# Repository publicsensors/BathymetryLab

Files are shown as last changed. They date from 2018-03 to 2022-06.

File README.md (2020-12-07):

# [Sound and the seafloor: Determining bathymetry using student-built acoustic sensors](https://doi.org/10.5670/oceanog.2020.305)

### Robert Levine<sup>1</sup>, Sasha Seroy<sup>1</sup>, and  Daniel Grünbaum<sup>1</sup>
<sup>1</sup> School of Oceanography, University of Washington, Seattle, WA, USA.

The article this repository supports was published in the September 2020 volume of <a href="https://doi.org/10.5670/oceanog.2020.305" target="_blank">*Oceanography*</a>.

This repository serves as a central location for the ultrasonic distance sensor Bathymetry Lab module and related activities for outreach, K-12, and undergraduate teaching. There are two sections to this repository, [**BathymetryLab**](https://github.com/publicsensors/BathymetryLab/tree/master/BathymetryLab) which contains the materials necessary to complete the seafloor activity, and [**AddOnsAndExtensions**](https://github.com/publicsensors/BathymetryLab/tree/master/AddOnsAndExtensions) which contains additional lab activities and code that can be used with the ultrasonic distance module.

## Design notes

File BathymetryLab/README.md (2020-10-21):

# BathymetryLab
## **MaterialsForInstructors**
### BathymetryLab_Instructor.ipynb
IPython notebook containing instructions and example figures for the bathymetry lab activity.
___
## **Handouts**
### BathymetryLab.ipynb
IPython notebooks for use to measure and map the change in seafloor using a JSN-SR04T waterproof transducer.  Students collect data at fixed intervals along a dock or pier and then create a plot of the bathymetry using python on their own computers. `BathymetryLab.ipynb` is the empty activity notebook.

### BathymetryLab_Pyserial.ipynb
Identical lab activity to `BathymetryLab.ipynb` however the notebook utilizes `pyserial` to record measurements directly from a USB-connected ESP8266 rather than requiring students to input readings by hand.
___
## **Microcontroller**
This folder contains the basic libraries and codes for using the HC-SR04 or JSN-SR04T acoustic sensor via MicroPython, though alternative microcontroller systems can be used to conduct the activity. Examples and code in this repository are for use with an ESP8266 processor microcontroller such as the [Feather HUZZAH with ESP8266](https://www.adafruit.com/product/2821).

Another example of sensor assembly using a [Feather STM32F405 Express](https://www.adafruit.com/product/4382) and [PyBoard](https://store.micropython.org/) microcontrollers can be found in the [Microcontroller Kits repository](https://github.com/publicsensors/MicrocontrollerKits/tree/master/Sensors/Acoustic) within the PublicSensors organization.

####  hcsr04.py
The driver for measuring distance using the HCSR04 sensor.  Required parameters are GPIO `trigger_pin` and `echo_pin`, with optional arguments for sound speed, `c`, and timeout. Private functions to intialize the sensor parameters and send signal.  `distance` function returns distance in millimeters.
```python
import hcsr04
sensor = hcsr04.HCSR04(trigger_pin=12, echo_pin=14, c=343) # define pins and speed of sound
sensor.distance() # returns distance in mm
```

#### firmware-combined.bin
Micropython firmware for ESP8266 boards. See [Getting started with MicroPython on the ESP8266](https://docs.micropython.org/en/latest/esp8266/tutorial/intro.html) for details on deploying the firmware.

#### boot.py
Basic boot initialization file example.

#### print_distance.py
Using the `hcsr04.py` driver to continuously measure and print distance at set interval.
```python
import print_distance
print_distance.print_distance(trigger_pin = 12, echo_pin = 14, c=343, interval=1) #interval is time in seconds
```
### SensorPartsList.xlsx
Excel spreadsheet with details and approximate pricing for sensor components needed to conduct the activity. Additional recommendations and instructions on assembly specific to this activity are found in the **MaterialsForInstructors** folder.

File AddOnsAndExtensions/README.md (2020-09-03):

# AddOnsAndExtensions

## **SpeedOfSound**
### SpeedOfSound_Instructor.ipynb
IPython notebook containing instructions and example figures for a lab activity to approximate the speed of sound in air using measurements collected at a fixed distance over variable values of `c`, sound speed.  Requires micropython firmware on ESP8266 or PyBoard microcontrollers and HC-SR04 sensor. `SpeedOfSound.ipynb` is the empty activity notebook.

### SpeedOfSound.ipynb
Contains all of the instructions for students to complete the assignment described above, but leaves out example executable code and data for figures.

### SpeedOfSound_Pyserial.ipynb
Identical lab activity to `SpeedOfSound.ipynb` however the notebook utilizes `pyserial` to record measurements directly from a USB-connected ESP8266 rather than requiring students to input readings by hand.

---

## **WaveTankLab**
Code for conducting an extension activity using multiple distance sensors to measure wave height at different positions in a wave tank. Students explore signal processing and implications of variable sampling frequencies.

### HCSR04_Timer.py
Runs HCSR04 to collect distance measurements at a fixed time interval using a periodic timer, with option to write to file.

###  HCSR04_TrigRx.py
Runs HCSR04 to collect distance measurements at a fixed time interval using a periodic timer, with option to write to file.  The timer is initiated from an external interrupt.

###  xcorrTimeSeries.py
Reads .txt files produced by HCSR04_Timer.py or HCSR04_SampleCt.py to create time series scatter plots of distance measurements.  User must define directory of file locations.

---

## **AdditionalCode**
Extra materials for reading and plotting recorded files.

### plot_recorded_distance.py
Reads and plots time series of distance data recorded in text file using `HCSR04_Timer.py` in the **WaveTankLab** or `record_distance.py`.

### record_distance.py
Using the hcsr04 driver to continuously measure distance at set interval and record to a text file. The output file can be read by the `plot_recorded_distance.py` script. Calling, as commented in the file, is completed as:
```Python
import record_distance
prefix = 'NAME'
interval_ms = 1 # sampling interval in milliseconds, 100 is 10Hz
record_time = 10 # time to record in seconds
trigger_pin_num = 12 # trigger pin connection to HCSR04 sensor
echo_pin_num = 14 # echo pin connection to HCSR04 sensor
sound_speed = 343 # Sound speed in m/s
write_file = 1

record_distance.record_dist(prefix,interval_ms,record_time, trigger_pin_num, echo_pin_num, sound_speed, write_file)
```

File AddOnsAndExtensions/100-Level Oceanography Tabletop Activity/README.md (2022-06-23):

# UW Oceanography Introduction to Environmental Monitoring and Technology (OCEAN 161)
This repository contains materials required to conduct the bathymetry lab acoustic sensor table top acitvity and lesson plan. This was conducted in a 100-level introductory oceanography course which focused on exploring tools and techniques scientists use to monitor the ocean and environment. This course is geared towards students with no prior oceanography or technology knowledge and enrolls many non-science majors. 

### Lab activity
`StudentWorksheet.docx` is the student activity sheet that walks through the lab procedure to build, calibrate, and simulate use to map bathymetry at two different spatial resolutions. The lab acitivity requires the `GraphingTemplate.xlsx` where students input their collected data and the template graphs it automatically to better facilitate data interpreatation and discussion. 

### Lab Preparation
To prepare for the lab, instructors must acquire the necessary parts and construct bathymetry boxes. In this iteration bathymetry boxes were constucted using black foam board and a seafloor feature was created within the box also using foam board. The boxes are 14" long x 10" tall x 4" wide and the faces are attached using hot glue. See photos below for top and side views of bathymetry boxes. 

topView    sideView

Electronic components needed include a Pyboard (or other microcontroller running MicroPython), jumper wires, and an hcsr-04 acoustic sensor. The microcontroller needs to be loaded with `hcsr04.py` and `distance_sensor.py`. Provided here are a file to 3D print a holder for the sensor, `SensorHolder.stl`,  to be able to slide it over the bathymetry box and create the table top bathymetry boxes required for the lab. Other materials needed include a ruler to calibrate the sensor, and an index card.

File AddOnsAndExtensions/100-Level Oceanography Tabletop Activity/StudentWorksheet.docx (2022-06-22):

Overview: In today’s lab, you will be building, calibrating, and using simple acoustic sensors to explore how sound is used in seafloor mapping applications. Work in lab groups of 3-4 students to complete this assignment.

Part 1: Build a simple acoustic sensor

The acoustic sensor you will use in this lab (HCSR-04) transmits sound and measures time elapsed until receiving it back. Using the speed of sound in the medium (e.g. in air, freshwater, or seawater) the sensor can calculate how far away an object or surface is just by measuring the time between sending out a sound, and receiving the echo. In this lab, we will just use the speed of sound in air (343 m/s).

Materials needed: acoustic sensor, four jumper wires, Pyboard microcontroller, USB cable, laptop

1. Connect the acoustic sensor to the microcontroller using jumper wires as shown below:

VCC (distance sensor) → V+ (Pyboard) | GND (distance sensor) → GND (Pyboard)
TRIG (distance sensor) → X10 (Pyboard) | ECHO (distance sensor) → X9 (Pyboard)

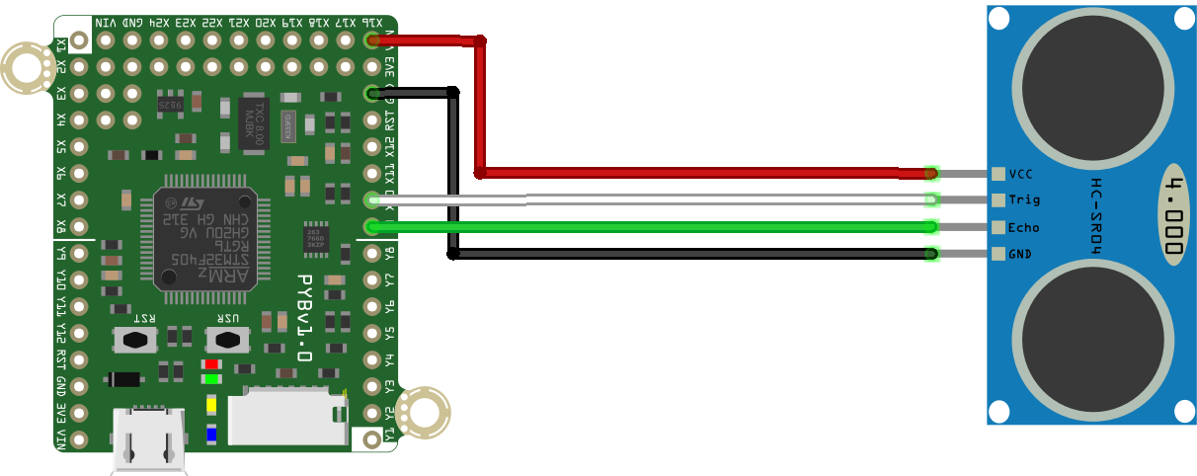
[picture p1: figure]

2. Connect the Pyboard to a laptop using the microUSB-USB cable. It should come up as a flashdrive. When you are ready to unplug your Pyboard after the lab, eject it properly just as you would a flashdrive.
3. In Google Chrome, launch the Beagle Term app and connect to your sensor. You can find this by searching the Chrome store or by searching “Beagle Term” in Google. This app lets you directly communicate with a microcontroller like the Pyboard you just attached the acoustic sensor to.

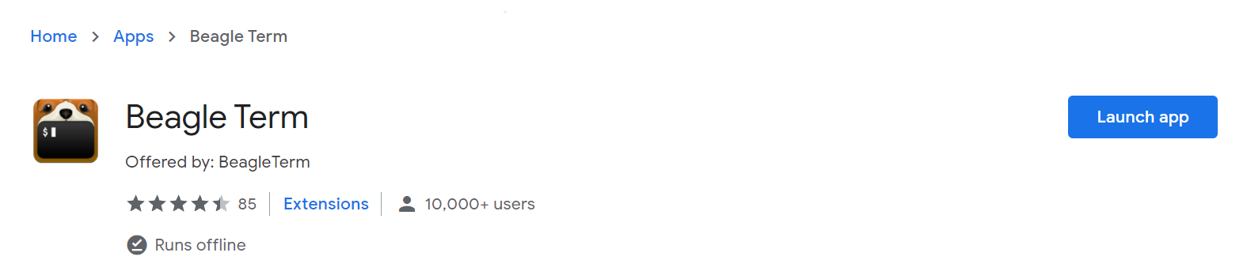
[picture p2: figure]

4. Beagle Term should automatically detect the settings you need. Click ‘Connect’ and make sure to click inside the window and press Enter. Note: If using a Mac, the Port may not automatically detect and you may need to try a few different ports in the drop down menu until you find the correct one that enables you to connect.

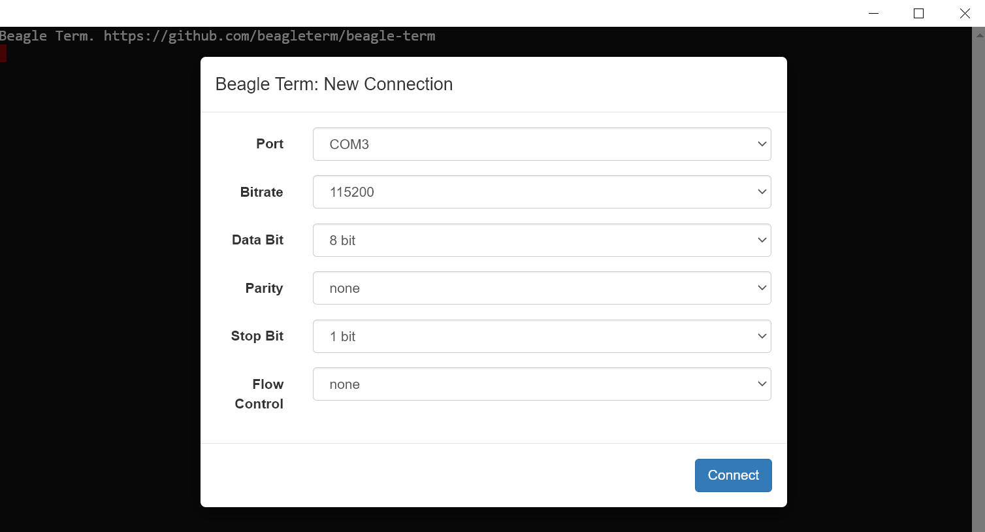
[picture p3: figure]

5. When you connect, the screen should look like the image below. The rectangular cursor after >>> indicates you are ready to type code. If you do not get this welcome screen use Ctrl+D to refresh the session.
6. In Beagle Term, type the following command and hit Enter to load the necessary function which will enable you to collect distance measurements. This command loads the function read_distance from the distance_sensor library on the Pyboard.
7. To get a distance measurement (in mm), use the read_distance function you just loaded by typing read_distance() and then hit Enter. A distance reading should print on the line below. To take another measurement, hit the up arrow to repeat the previous command without retyping it.

Test out your sensor by moving your hand closer to the sensor and then take a reading. Then move your hand and farther away and take another reading. Observe how the distance detected from your hand to the sensor changes.

Part 2: Calibrate the acoustic sensor (40pts)

Materials needed: Constructed acoustic sensor, ruler, index card

You will now assess the accuracy of the acoustic sensor you just built. This is known as calibration. To calibrate an instrument, you compare against a known standard. Since your sensor measures distance acoustically, you can compare it to a ruler (a known standard of distance).

1. Place a ruler on the table with the distance sensor set at zero 0 mm.
2. Place an index card 5cm (50mm) away from the sensor and take 5 replicate readings. Record readings in the table below and calculate the mean distance based on your 5 readings. Repeat the process for each of the distances listed below. (12pts)

Ruler distance (mm) | Sensor Distance 1 (mm) | Sensor Distance 2 (mm) | Sensor Distance 3 (mm) | Sensor Distance 4 (mm) | Sensor Distance 5 (mm) | Mean Distance (mm)
50
100
150
200
250
300

3. Assess the precision of your acoustic sensor using your distance data from 200mm. Recall that calculating the standard deviation of your measurements will give you a measure of precision. Show your work. (4pts)

Standard deviation (σ) = measure of the spread of a set of data points | σ= √((Σ(x_i - μ)^2)/n)

n = number of values in set x_i = each value from the set

4. What does this mean about how repeatable or precise your distance measurements are? (2pts)
5. Create a calibration curve for your acoustic sensor. This will help you assess the accuracy of your sensor. Accuracy is a measure of how close your sensor readings are to the true value (ruler measurement). To create the calibration curve, make a graph of the ruler distance vs. the mean measured distance using the six points from your table above. Use the Excel template (Tab 1) to help you. Open the spreadsheet locally in Excel, not in Google Sheets to preserve the functionality. Attach the Excel file with completed graph to your assignment submission. (12pts)
6. Report the equation of the trendline for your calibration. What does the slope mean about the calibration? What does the intercept mean about the calibration? (5pts)
7. Using your answers above, how accurate do you think your acoustic sensor is? (3pts)
8. Are there any differences in your sensor’s accuracy when reading short vs. long distances? How do you know? (2pts)

Part 3: Use the acoustic sensor to map the seafloor (48pts)

In this part you will use your sensor to measure the height of the seafloor along a transect using a Bathymetry Box. Inside the Bathymetry Box is a replica of a seafloor feature you will try to map using your acoustic sensor. This is analogous to how oceanographers map seafloor features from a ship on the surface.

1. Get a Bathymetry Box and identify the measuring tape along the top of it. This will help you plan out where to take distance measurements.
2. Insert the acoustic sensor facing downward into the frame which will slide along the top of the box.
3. Take distance measurements every three inches and record them in a table. Like you did in Part 2, take 5 replicate readings at each sampling position, and calculate the mean. (8pts)

Length along transect (inches) | Sensor Distance 1 (mm) | Sensor Distance 2 (mm) | Sensor Distance 3 (mm) | Sensor Distance 4 (mm) | Sensor Distance 5 (mm) | Mean Distance (mm)
1”
4”
7”
10”
13”

4. Now increase the spatial resolution of your measurements. Take distance measurements as you did above every inch and record them in the table below. (16pts)

Length along transect (inches) | Sensor Distance 1 (mm) | Sensor Distance 2 (mm) | Sensor Distance 3 (mm) | Sensor Distance 4 (mm) | Sensor Distance 5 (mm) | Mean Distance (mm)
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
When you are ready to unplug your Pyboard after the lab, eject it properly just as you would a flashdrive. Do not just unplug it!!!

5. Create a graph which combines the data from the above two tables. Plot length along transect vs. the mean depth calculated using your acoustic sensor. Use the Excel Template (Tab 2) to help you. Open the spreadsheet locally in Excel, not in Google Sheets to preserve the functionality. Attach the Excel file with completed graph to your assignment submission. (12pts)
6. How did increasing the resolution of your measurements affect your ability to characterize the bathymetry? Provide an example from your graph. (5pts)
7. What feature(s) could you identify from your acoustics measurements? (3pts)
8. What would be the ideal spatial resolution to sample the transect you sampled? Why? (2pts)

Reflection questions (12pts)

a. What are the overall benefits of using these acoustic tools? (3pts)
b. What are the overall limitations of using these acoustic tools? (3pts)
c. Over what time and space scales could these acoustic tools be helpful to observing the environment? (4pts)

Feedback: What did you think of this lab? What did you learn from it? Did you enjoy it? What can be improved? (2 pts)

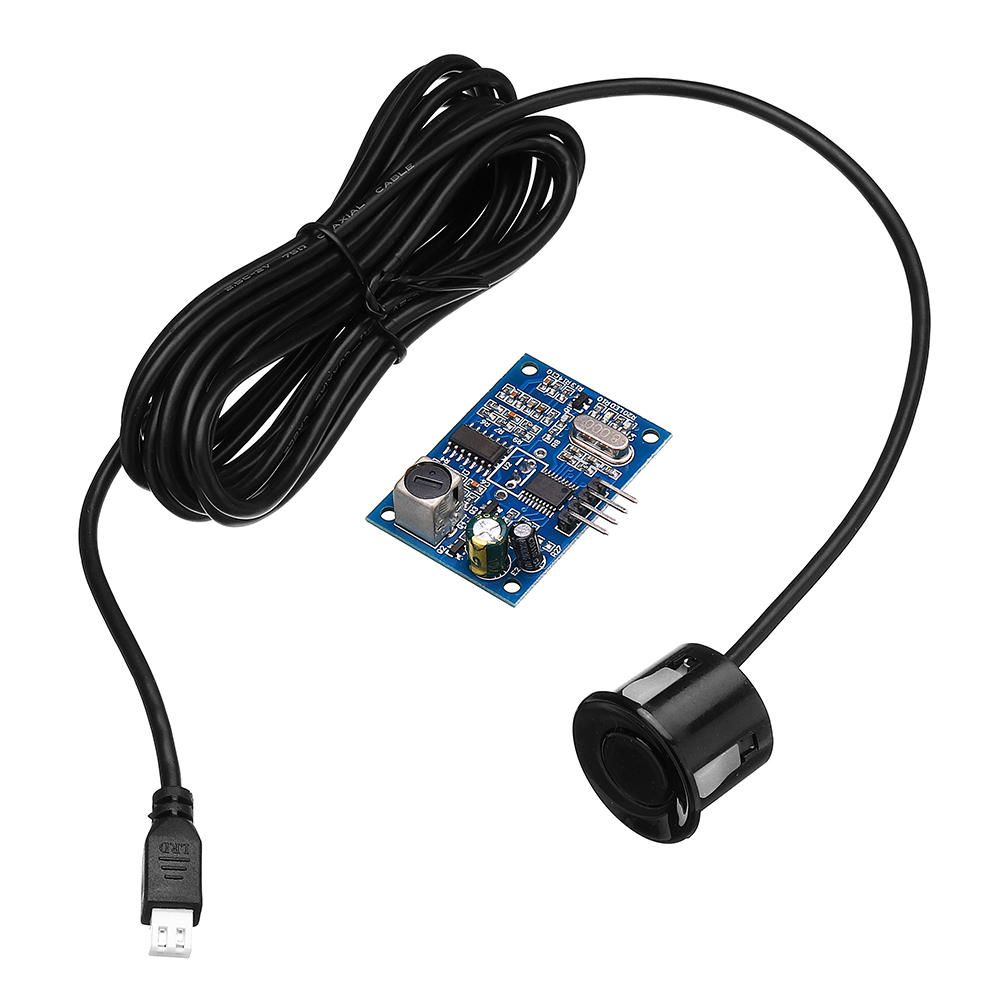
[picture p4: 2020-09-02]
images/jsnsr04.png

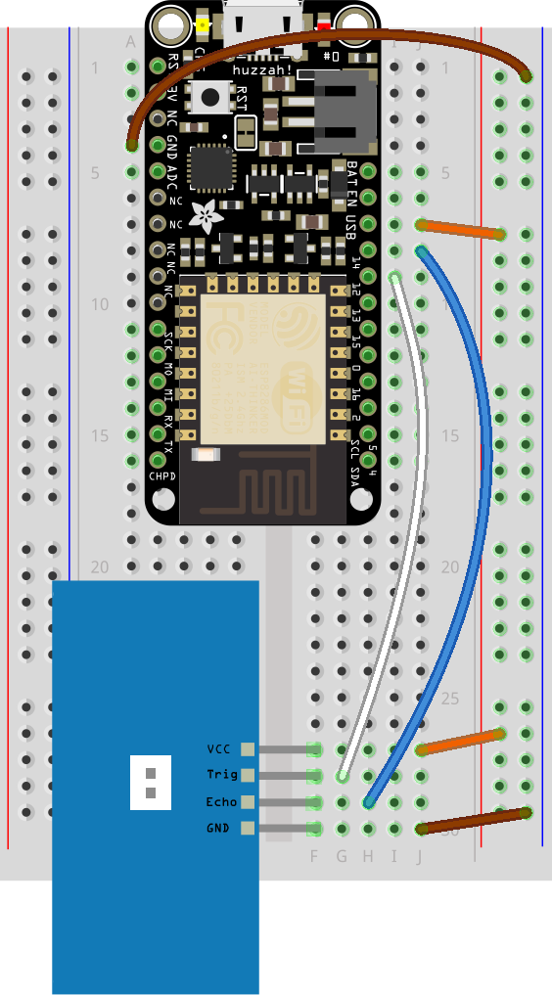
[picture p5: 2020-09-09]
images/Feather_jsnsr04.png

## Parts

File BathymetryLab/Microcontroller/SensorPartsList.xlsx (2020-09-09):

For a class of 20 students
Total 12 kits (10 groups of 2 students + 2 extra kits just in case)
Sensor components | Cost ($) | Number | Total ($) | Notes | Link for example materials
Feather HUZZAH with ESP8266 | 16.95 | 12 | 203.4 | *See Below | https://www.adafruit.com/product/2821
M-M jumpers (pack of 20) | 1.95 | 4 | 7.8 | **See Below | https://www.adafruit.com/product/1956
JSN-SR04T Waterproof Ultrasonic Module | 10.95 | 12 | 131.4 |  | https://www.jameco.com/z/JSN-SR04T-Arndt-Waterproof-Ultrasonic-Module-JSN-SR04T-Integrated-Distance-Measuring-Transducer-Sensor-for-Arduino_2279255.html
microUSB cable | 2.95 | 12 | 35.4 |  | https://www.adafruit.com/product/592
Half-size bradboard | 5 | 12 | 60 | **See Below | https://www.adafruit.com/product/64
Total ($) |  |  | 438
Additional
*Boards ship with header pins which will need to be soldered for use with either a breadboard or F-F jumpers for connection to the distance module.
**In place of a breadboard, students can use F-F jumpers to directly connect the JSN-SR04T module to the header pins of the microcontroller (https://www.adafruit.com/product/1950).

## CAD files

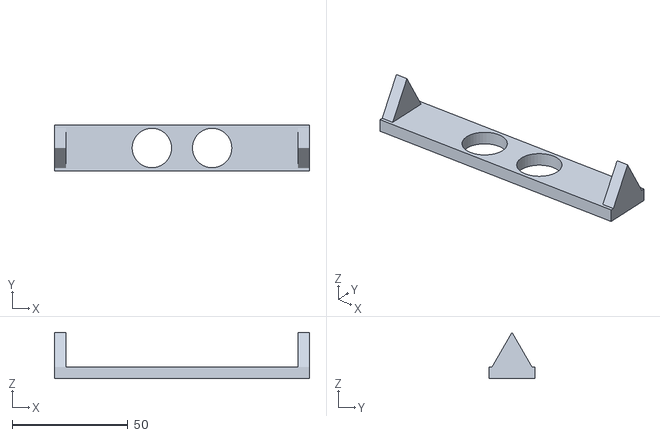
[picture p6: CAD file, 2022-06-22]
AddOnsAndExtensions/100-Level Oceanography Tabletop Activity/SensorHolder.stl
110.0 x 20.0 x 20.0

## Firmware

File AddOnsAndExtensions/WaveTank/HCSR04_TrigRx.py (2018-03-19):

#
#  Collect data from an HCSR04 ultrasonic sensor by setting a timer to sample at
# a fixed interval for a given length of recording
   # Free up heap space

"""
# Before calling HCSR04_TrigRx, the rtc on the ESP8266 must be synced with NTP:

from network import WLAN, STA_IF
wlan = WLAN(STA_IF)
wlan.active(True)
wlan.connect('OTCnet','ocN3five1_OTc')
import ntptimeTS3231
ntptimeTS3231.settime()

# Once the onboard clock is set, we have to define all of the parameters for running
#  An example of a typical execution sequence:
#---------------------------------------
# Sampling parameters - must be defined
#---------------------------------------
 	
import HCSR04_TrigRx

prefix = 'Position2_SlowWave'
interval_ms = 100 # sampling interval in milliseconds, 100 is 10Hz
record_time = 60 # time to record in seconds
trigger_pin_num = 12 # trigger pin connection to HCSR04 sensor
echo_pin_num = 13 # echo pin connection to HCSR04 sensor
sound_speed = 343 # Sound speed in air in m/s
write_file = 1 # 0 to just print values, 1 to save to text file with file prefix defined above

HCSR04_TrigRx.measure_dist(prefix,interval_ms,record_time,
trigger_pin_num, echo_pin_num, sound_speed, write_file)

"""

#
from machine import RTC, Pin, Timer, unique_id
import utime
from ubinascii import hexlify
from gc import collect
from hcsr04 import HCSR04
from os import rename, listdir
collect()

def measure_dist(prefix='ocn351',interval_ms=100, record_time = 5,trigger_pin_num = 12, echo_pin_num=13, sound_speed=343, write_file = 0):
	global startSampleFlag
	startSampleFlag = 0
	sensor = HCSR04(trigger_pin = trigger_pin_num, echo_pin = echo_pin_num, c=sound_speed) # Set up the HCSR04
        print('\nUsing sampling interval ',interval_ms,' milliseconds...')
	print('Recording data for ',record_time,' seconds...\n')
	print('\n\n****Beginning Recording ****\n\n')
	runTimer = Timer(-1) # Initiate a timer
	tmp_file='tmp.txt'  # A temporary filename; we will write partial data to this file, and rename only if sampling
	rtc = RTC() # intiate a real-time clock variable
	ID=hexlify(unique_id()).decode('utf-8') # Unique ID of the microprocessor
	timestamp=str(utime.mktime(rtc.datetime())) # Create a string time stamp from the real-time clock
	filename=prefix+'_'+ID+'_'+timestamp+'.txt' # Define a filename to be used if writing a file
	if write_file ==1: # If writing a file...
		print('\nCreating data file: ',filename,'\n\n') # Notify user
		datafile=open(tmp_file,'w')  # Create and open a temporary file for data to be logged to
	else: # if not writing a file...
		datafile='' # Create an empty variable to be passed along
		print('\nNot writing data to file\n') # Notify user
	# Run a timer that executes our record_dist function periodically, with the interval of the period defined from interval_ms
	print('\nWaiting For Trigger\n')
	while True:
		if startSampleFlag==1:
			startSampleFlag=0
			init_record(runTimer, record_time,interval_ms, sensor,write_file, tmp_file, rtc, datafile, filename)

def RunTrigger(p): # set the trigger):
	global startSampleFlag
	startSampleFlag = 1

def init_record(runTimer, record_time,interval_ms, sensor,write_file, tmp_file, rtc, datafile, filename):
	runTimer.init(period=interval_ms, mode=Timer.PERIODIC, callback=lambda t:record_dist(sensor,write_file, rtc, datafile))
	utime.sleep(record_time) # Sleep and let the timer run for the length of time defined by record_time
	runTimer.deinit() # At the end of our sleep, stop the timer
	if write_file ==1:	# If we've been writing a file...
		datafile.close() # Close the temporary file
		rename(tmp_file,filename) # Rename the temporary file with the filename constructed above

# The actual function taking a measurement and recording the time
def record_dist(sensor,write_file, rtc, datafile): # requires the sensor, real-time clock, and datafile handles, and whether we are writing a file
	led = Pin(2,Pin.OUT)
	led.value(0)
	t_onboard=rtc.datetime() # Get the time
	dist = sensor.distance() # take a distance measuremen
	if write_file ==1: # If saving the data...
		data_str='' # Initiate a string to add values to
		for t in [t_onboard[0],t_onboard[1],t_onboard[2],t_onboard[4],t_onboard[5],t_onboard[6],t_onboard[7], dist]: # for each value in the date string plus measurement...
			data_str+='{} '.format(t) # Combine all of the values into one line
		df=datafile.write("%s\n" % data_str) # What that line and a line-break into our file
	# Whether writing a file or not, print the time and measurement for the user to see
	print(t_onboard[0],t_onboard[1],t_onboard[2],t_onboard[4],t_onboard[5],t_onboard[6],t_onboard[7], dist)
	led.value(1)

global startSampleFlag
p14 = Pin(14, mode = Pin.IN, pull = Pin.PULL_UP) # define my interrupt input
p14.irq(trigger=Pin.IRQ_RISING, handler=RunTrigger) # set the trigger

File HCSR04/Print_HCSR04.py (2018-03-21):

'''
Run and print readout from an HCSR04 sensor using an ESP8266 (micropython controller)
in centimeters.  The sensor will print and read values at a given interval until
broken by the user (ctrl+c)
'''

from machine import Pin
import utime
from hcsr04 import HCSR04

sound_speed = 343
trigger_pin_num=12
echo_pin = 14
sleep_time  = 1

def print_HCSR04(trigger_pin = trigger_pin_num, echo_pin = echo_pin_num, c=sound_speed, interval=sleep_time):
    sensor = HCSR04(trigger_pin, echo_pin, c)
    led = Pin(2, Pin.OUT)
    led.value(0)
    while True:
        led.value(1)
        print(sensor.distance())
        utime.sleep(interval)

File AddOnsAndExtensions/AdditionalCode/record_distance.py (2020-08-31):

#
#  Collect data from an HCSR04 ultrasonic sensor by defining the sample interval
#  and total time to record.  Write a file if requested.
#
from machine import RTC, Pin, unique_id
import utime
from ubinascii import hexlify
from gc import collect
from hcsr04 import HCSR04
from os import rename
collect()      # Free up heap space

"""
#  An example of a typical execution sequence:
#---------------------------------------
# Sampling parameters
#---------------------------------------

import record_distance

prefix = 'NAME'
interval_ms = 1 # sampling interval in milliseconds, 100 is 10Hz
record_time = 10 # time to record in seconds
trigger_pin_num = 12 # trigger pin connection to HCSR04 sensor
echo_pin_num = 14 # echo pin connection to HCSR04 sensor
sound_speed = 343 # Sound speed in m/s
write_file = 1

record_distance.record_dist(prefix,interval_ms,record_time, trigger_pin_num, echo_pin_num, sound_speed, write_file)

"""

def record_dist(prefix='NAME',interval_ms=100,record_time=10, trigger_pin_num = 12, echo_pin_num=14, sound_speed=343, write_file = 1):
	rtc = RTC()
	sensor = HCSR04(trigger_pin = trigger_pin_num, echo_pin = echo_pin_num, c=sound_speed)
	print('\nUsing sampling interval ',interval_ms,' milliseconds...')
	print('Recording data for ',record_time,' seconds...\n')
	ID=hexlify(unique_id()).decode('utf-8') # Unique ID of the microprocessor
	tmp_file='tmp.txt'  # A temporary filename; we will write partial data to this file, and rename only if sampling
	datafile=open(tmp_file,'w')
	print('\n\n****Beginning Recording ****\n\n')

	timestamp=str(utime.mktime(rtc.datetime()))
	if write_file ==1:
		filename=prefix+'_'+ID+'_'+timestamp+'.txt'
		print('\nCreating data file: ',filename)
	sample_num = (record_time*1000)/100

	for sample in range(sample_num+1):
		t_onboard=rtc.datetime()
		dist = sensor.distance()
		data_str=''
		print(dist)
		if write_file ==1:
			for t in [sample,t_onboard[0],t_onboard[1],t_onboard[2],t_onboard[4],t_onboard[5], \
						   t_onboard[6],t_onboard[7], dist]:
				data_str+='{} '.format(t)
			if sample==0:
				datafile=open(tmp_file,'w')
			else:				# If the first sample, overwrite old tmp_file if it exists
				df=datafile.write("%s\n" % data_str) # df contains the "result" of the write statement (success or failure)

		else:
			print(sample,t_onboard[0],t_onboard[1],t_onboard[2],t_onboard[3],t_onboard[4],t_onboard[5], \
						  t_onboard[6],t_onboard[7], dist)
		if sample<sample_num:  # Sleep only if another sample is to be taken
			utime.sleep_ms(interval_ms)

		#---------------------------------------
		# Done with the comparison loop; change the temporary filename to the permanent one, now that sampling is complete
	if write_file ==1:	#---------------------------------------
		datafile.close()
		rename(tmp_file,filename)

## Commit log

2018-03-21 Added example of just printing out measurements in a while loop
2020-09-03 sensor parts list
    [SensorPartsList.xlsx]
2020-09-04 student data sheet
    [StudentDataSheet.xlsx]
2020-09-08 update V+ to USB
    [SensorPartsList.xlsx]
